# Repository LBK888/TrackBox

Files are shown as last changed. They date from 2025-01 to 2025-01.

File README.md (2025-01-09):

# TrackBox: An Open-Source Larvae Tracking and Monitoring System
For imaging zebrafish 6~7 dpf old zebrafish larvae

This project builds upon our preliminary research to further design and develop a versatile and cost-effective larvae tracking photography box compatible with 6-well and 24-well plates. 
The software includes a Python application for imaging and an Arduino IDE script for temperature and humidity recording. 
The initial versions of the software are openly available on here, while the hardware design is being updated to version 2.0:


## Key Features
- **Cost-Effective and Compatible**  
  Compatible with 6-well and 24-well plates, with material costs under 5000 TWD. For experiments using 6–7 days post-fertilization (dpf) zebrafish, each well can hold 5–7 fish, adjustable to 1–10 fish per well as needed.
- **Foldable and Portable Design**  
  The hardware features a foldable structure (Figure 14, bottom left), facilitating easy shipment to collaborating laboratories that cannot fabricate it themselves.  
- **Open Source**  
  Both hardware and software are open source and available on GitHub, with ongoing updates aligned with project milestones.  

## Technical Specifications
- **Camera**: SONY IMX179 sensor supporting 2592×1944 resolution at 20 fps. USB UVC-compatible, requiring no drivers for direct usage.  
- **Environment Monitoring**: Equipped with an AHT10 sensor to record temperature and humidity during imaging, ensuring experiments are conducted under stable environmental conditions.  
- **Lighting**: The base features an LED white light panel for uniform illumination.  
- **Multi-Box Support**: The imaging software supports simultaneous operation with 2–4 photography boxes, enhancing experimental efficiency.  

This system significantly reduces experimental costs and improves efficiency for zebrafish locomotion behavior studies. Contributions, feedback, and collaborations are welcomed!

## DIY Parts
- **3D printing**: See 3D parts folder
- **Laser cutting**: See Laser parts folder

## Electrical Parts
- **Camera**: USB 800 Megapixels ([DFROBOT FIT0729](https://www.dfrobot.com/product-2188.html))
- **Light box**: 15cm *2 - 5V COB 6000k (white light) LED stripe (5mm wide, 400 LED/meter), or 5050 LEDs 
- **Sensor**: (optional) temperature and humidity sensor, [AHT10](https://a.co/d/ckcVx5F)
- **MCU**: (optional) for temp+humid [D1 mini](https://a.co/d/eWSJpXV)

## Installation
Please read this [pdf manual](UpperPartInstructions.pdf) to assemble the upper part

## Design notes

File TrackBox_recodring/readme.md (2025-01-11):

# IMX179 Recording Program

## Overview
This program is designed for recording videos using the IMX179 camera (DFRobot FIT0729) along with temperature and humidity data collection. It supports the TrackBox v2.0 framework and is optimized for high-resolution video recording and real-time environmental data monitoring.

---

## Features
- **Camera Specifications**:
  - Max Resolution: 3264x2448 (8 Megapixels)
  - Video Output Format: AVI
  - Supported Resolutions & Frame Rates:
    - 3264x2448 @ 15fps
    - 2592x1944 @ 15fps
    - 1920x1080 @ 30fps
    - Additional resolutions supported.

- **Environment Data Logging**:
  - Reads temperature and humidity data via a serial connection.
  - Supports export to `.xlsx` files and visualizes data with plots.

- **Customizable Settings**:
  - Adjustable resolution, exposure, and recording duration.
  - Automatic and manual exposure control.
  - Configurable file output directories.

---

## Tested condition
- **Operating System**: Windows 11
- **Python Version**: 3.12.6
- **Hardware**: 
  - IMX179 Camera (DFRobot FIT0729)
  - MCU + AHT10 device for environment data collection (e.g., CH340 module)

### Python Dependencies
Install the required packages from the provided `requirements.txt` file:
pip install -r requirements.txt

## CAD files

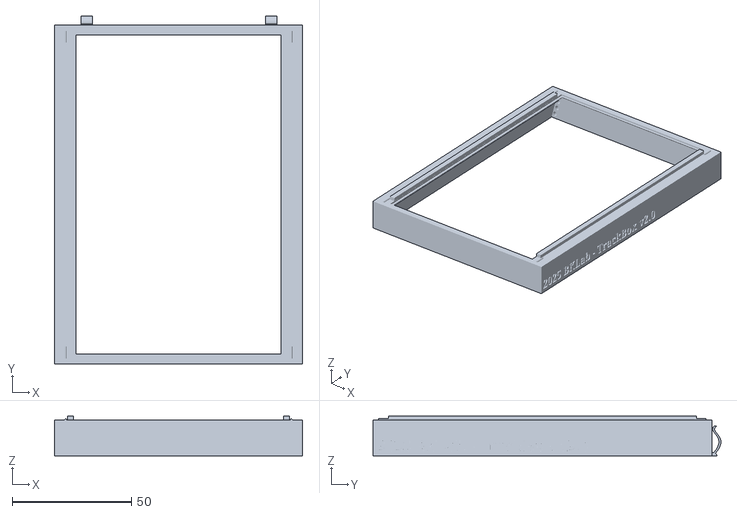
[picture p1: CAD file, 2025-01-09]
3D parts/LightBox v2.0_LightBox.stl
104.0 x 145.8 x 16.7

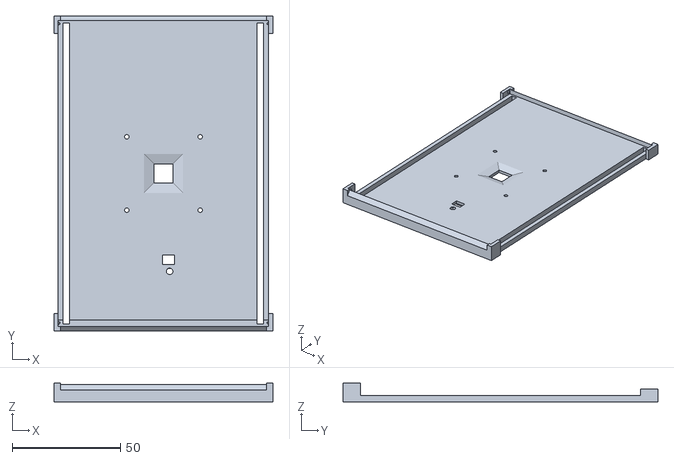
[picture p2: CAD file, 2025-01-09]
3D parts/LightBox v2.0_top2.stl
101.3 x 145.5 x 8.60

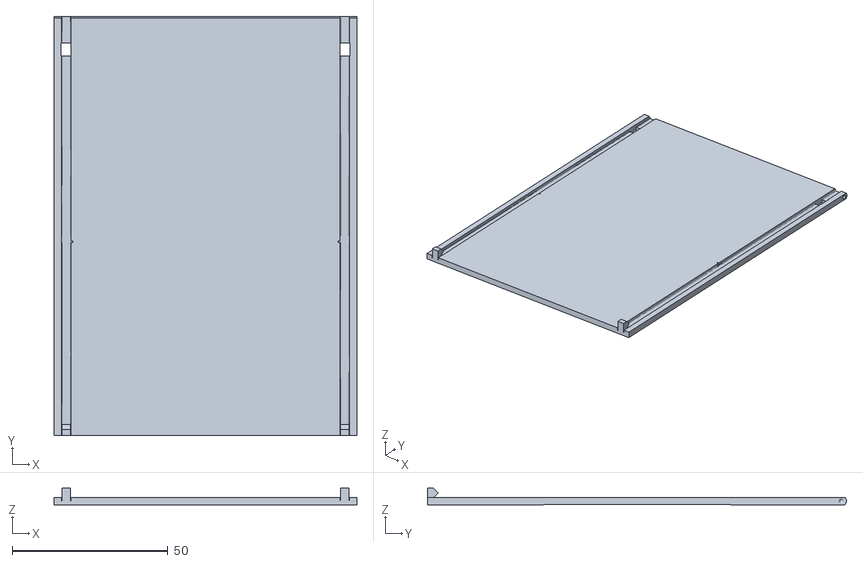
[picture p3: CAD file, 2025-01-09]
3D parts/LightBox v2.0_tall side.stl
97.2 x 134.5 x 5.30

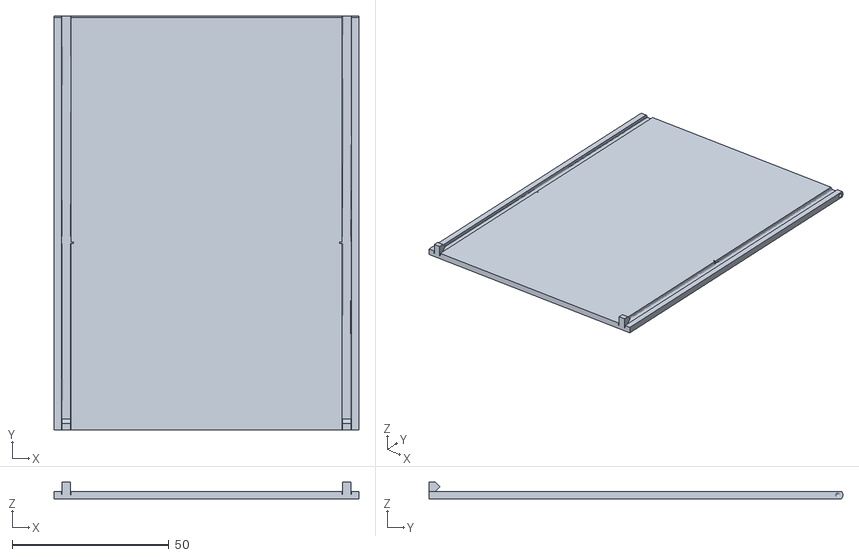
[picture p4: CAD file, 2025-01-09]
3D parts/LightBox v2.0_short side.stl
97.2 x 132.0 x 5.30

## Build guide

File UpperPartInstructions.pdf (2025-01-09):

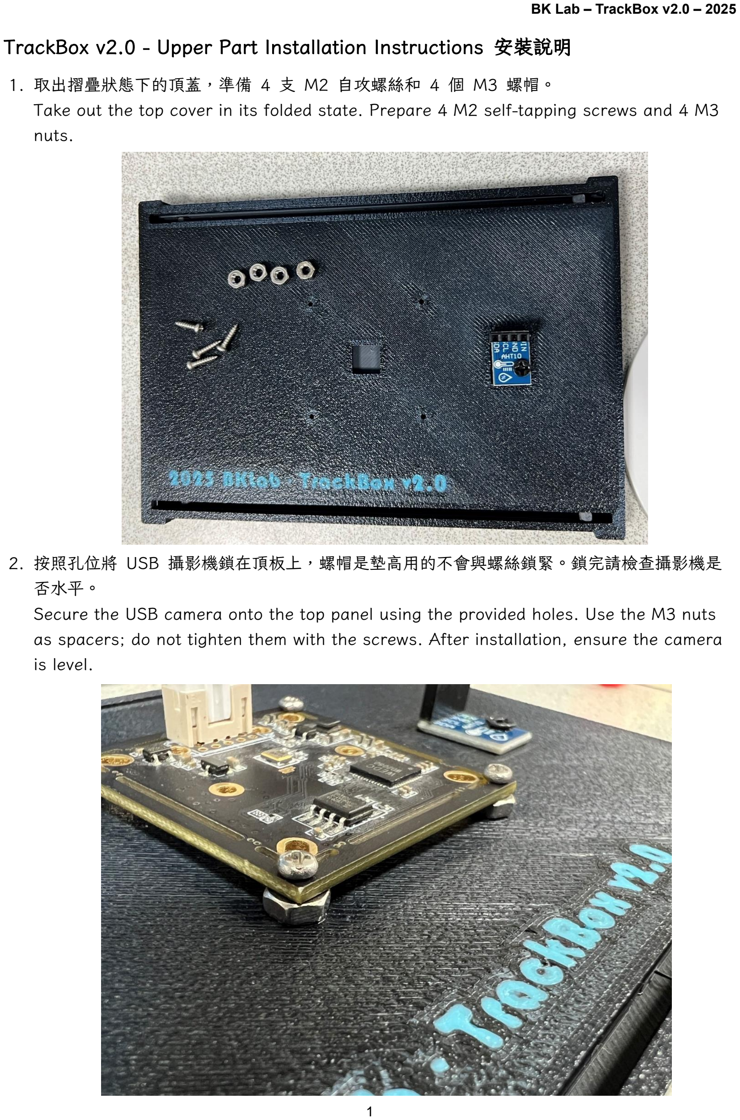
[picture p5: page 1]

BK Lab – TrackBox v2.0 – 2025
TrackBox v2.0 - Upper Part Installation Instructions 安裝說明
1. 取出摺疊狀態下的頂蓋，準備 4 支 M2 自攻螺絲和 4 個 M3 螺帽。
Take out the top cover in its folded state. Prepare 4 M2 self-tapping screws and 4 M3 nuts.
2. 按照孔位將 USB 攝影機鎖在頂板上，螺帽是墊高用的不會與螺絲鎖緊。鎖完請檢查攝影機是 否水平。
Secure the USB camera onto the top panel using the provided holes. Use the M3 nuts as spacers; do not tighten them with the screws. After installation, ensure the camera is level.

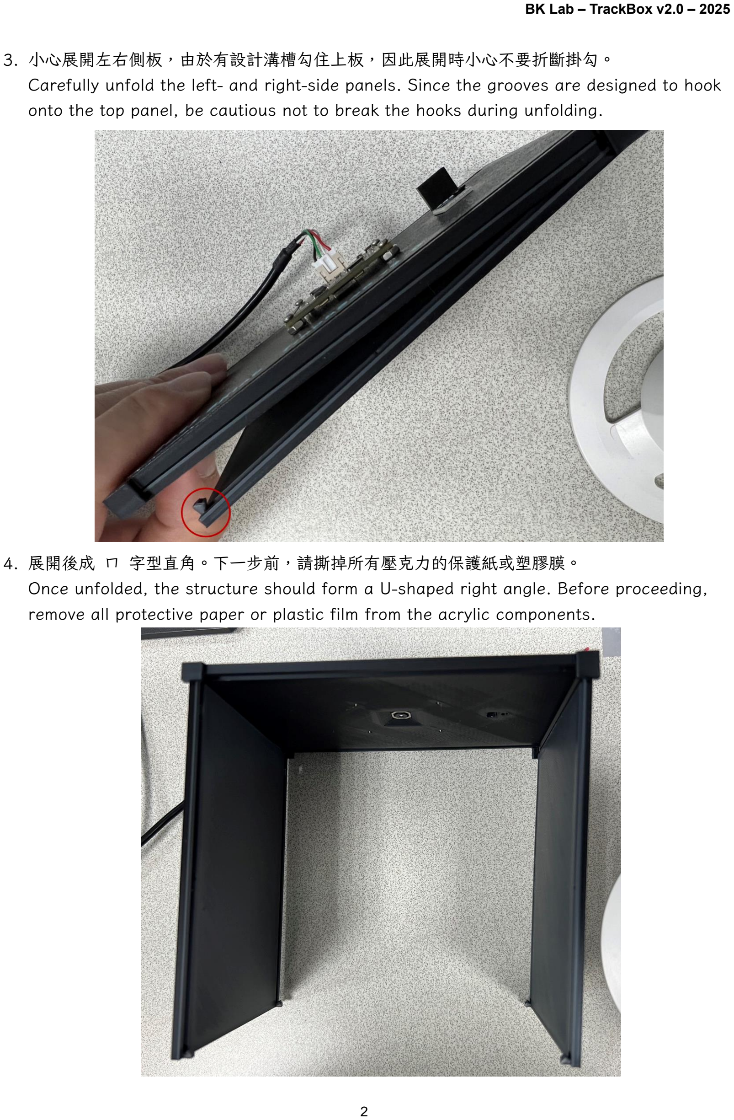
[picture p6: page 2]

3. 小心展開左右側板，由於有設計溝槽勾住上板，因此展開時小心不要折斷掛勾。 Carefully unfold the left- and right-side panels. Since the grooves are designed to hook onto the top panel, be cautious not to break the hooks during unfolding.
4. 展開後成 ㄇ 字型直角。下一步前，請撕掉所有壓克力的保護紙或塑膠膜。
Once unfolded, the structure should form a U-shaped right angle. Before proceeding, remove all protective paper or plastic film from the acrylic components.

5. 插入前後壓克力板，可選兩片皆不透光全黑色，或前側使用半透光。壓克力非亮面要朝向攝影 和內部以減少反光。
注意：這個步驟由於密合度高所以最為困難，請嘗試讓壓克力板剛進入時保持兩側深度一致。 如果左右側板被壓克力板推至脫落，請再左右側板卡回去即可。

Insert the front and rear acrylic panels. You can choose either fully opaque black panels for both or a semi-transparent panel for the front. Ensure the non-glossy side of the acrylic faces inward and toward the camera to reduce reflections.
Note: This step may be challenging due to the tight fit. If the side panels come loose, simply reattach them.
6. 前後壓克力板插入完成後，請注意前後面的四個接觸角落是否密合，確保攝影盒沒有形變。 After inserting the front and rear acrylic panels, check the four corner connections to ensure a tight fit. This ensures the photography box maintains its intended shape.

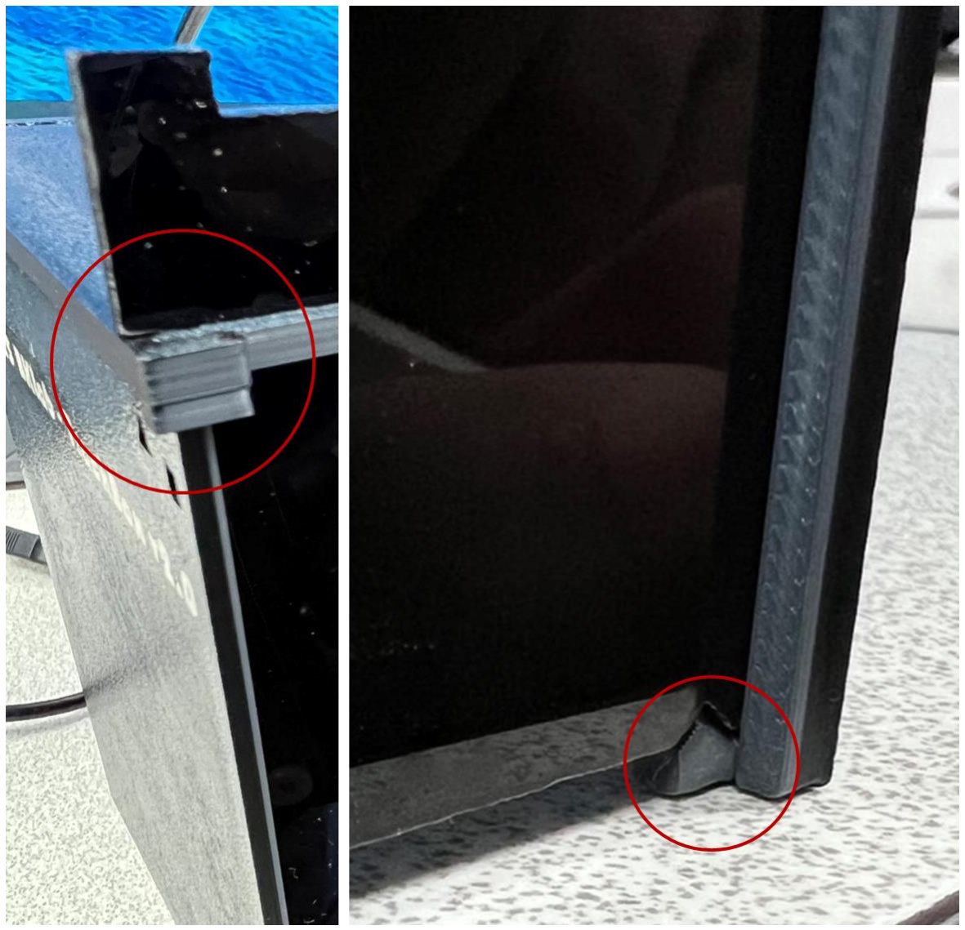
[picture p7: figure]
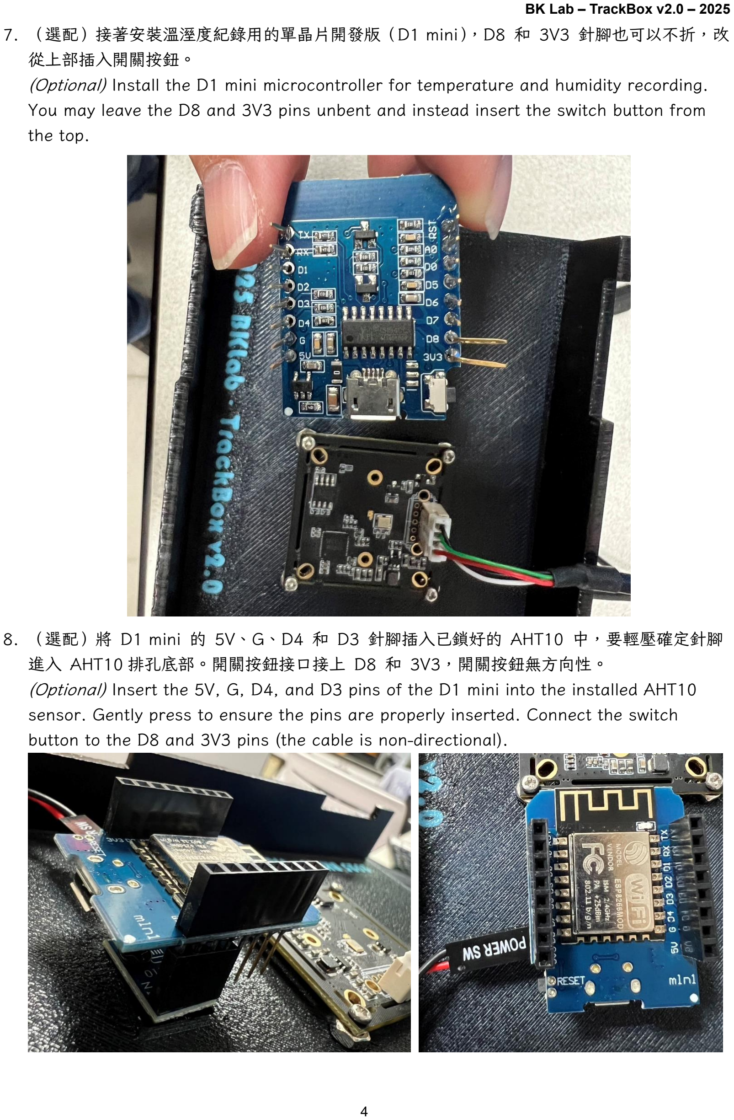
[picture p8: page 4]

7. （選配）接著安裝溫溼度紀錄用的單晶片開發版（D1 mini），D8 和 3V3 針腳也可以不折，改 從上部插入開關按鈕。
(Optional) Install the D1 mini microcontroller for temperature and humidity recording. You may leave the D8 and 3V3 pins unbent and instead insert the switch button from the top.
8. （選配）將 D1 mini 的 5V、G、D4 和 D3 針腳插入已鎖好的 AHT10 中，要輕壓確定針腳 進入 AHT10 排孔底部。開關按鈕接口接上 D8 和 3V3，開關按鈕無方向性。 (Optional) Insert the 5V, G, D4, and D3 pins of the D1 mini into the installed AHT10 sensor. Gently press to ensure the pins are properly inserted. Connect the switch button to the D8 and 3V3 pins (the cable is non-directional).

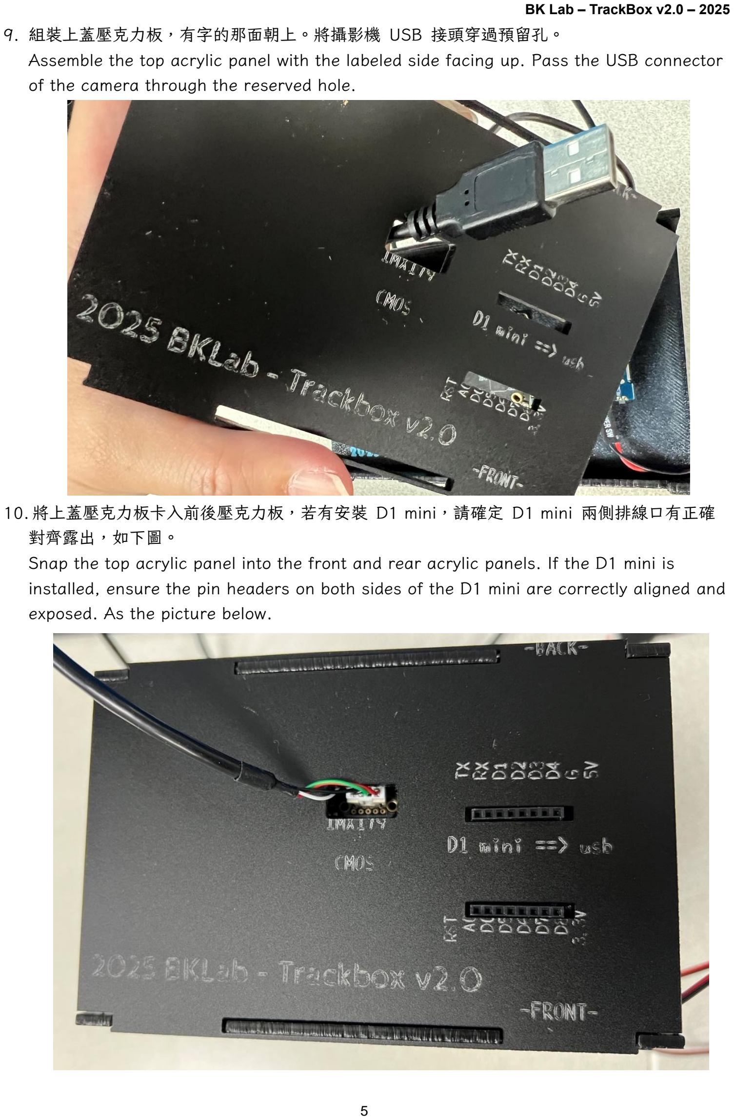
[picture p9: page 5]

9. 組裝上蓋壓克力板，有字的那面朝上。將攝影機 USB 接頭穿過預留孔。
Assemble the top acrylic panel with the labeled side facing up. Pass the USB connector of the camera through the reserved hole.
10. 將上蓋壓克力板卡入前後壓克力板，若有安裝 D1 mini，請確定 D1 mini 兩側排線口有正確 對齊露出，如下圖。
Snap the top acrylic panel into the front and rear acrylic panels. If the D1 mini is installed, ensure the pin headers on both sides of the D1 mini are correctly aligned and exposed. As the picture below.

11. （選配）將 D1 mini 接上 micro USB 線，連上電腦，序列埠通訊 115200 baud 可看到溫 溼度感測器資訊，如下圖。
(Optional) Connect the D1 mini to a computer using a micro USB cable. Use serial communication at 115200 baud to view the temperature and humidity sensor readings. As the picture below.

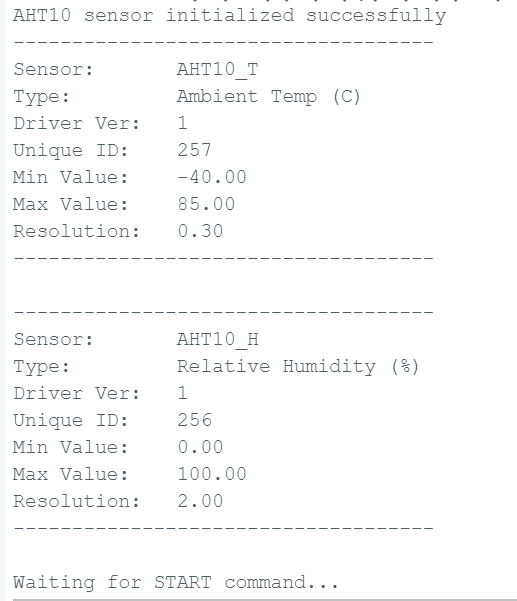
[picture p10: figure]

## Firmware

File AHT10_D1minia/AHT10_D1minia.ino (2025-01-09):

#include <Wire.h>
#include <Adafruit_AHT10.h> // 使用 AHT10 的庫，需要先安裝 (可從 Library Manager 搜尋 "AHT10")

#define SDA_PIN D3         // I²C SDA 腳位
#define SCL_PIN D4         // I²C SCL 腳位
#define BUTTON_PIN D8      // 按鈕開關接 D8 (GPIO15)
#define LED_PIN D2      // 測量指示燈, LED_BUILTIN=D4已經被佔據 


Adafruit_AHT10 aht10;               // 初始化 AHT10 物件
Adafruit_Sensor *aht_humidity, *aht_temp;

bool isMeasuring = false;  // 測量狀態標誌
float filter_r=0.3;     //smoothing filter, 前一次數據，站新數據的filter_r, recommand = 0.2~0.5
float temperature_rec=0.0;
float humidity_rec=0.0;

void setup() {
  // 初始化序列埠
  Serial.begin(115200);
  while (!Serial); // 等待序列埠初始化（適用於部分開發板）

  //Measuring LED
  pinMode(LED_PIN, OUTPUT);  // Initialize the LED_PIN pin as an output

  // 初始化按鈕腳位
  pinMode(BUTTON_PIN, INPUT); // 按鈕接 3.3V，利用內建下拉電阻

  // 初始化 I²C
  Wire.begin(SDA_PIN, SCL_PIN);
  Serial.println("I2C Initialized");

  // 初始化 AHT10
  if (aht10.begin()) {
    Serial.println("AHT10 sensor initialized successfully");
  } else {
    Serial.println("Failed to initialize AHT10 sensor!"); 
    while (1) { 
      delay(50);   // 如果感測器初始化失敗，停止執行
    }
  }

  aht_temp = aht10.getTemperatureSensor();
  aht_temp->printSensorDetails();

  aht_humidity = aht10.getHumiditySensor();
  aht_humidity->printSensorDetails();

  Serial.println("Waiting for START command...");


    //  /* Get a new normalized sensor event */
    sensors_event_t humidity;
    sensors_event_t temp;
    aht_humidity->getEvent(&humidity);
    aht_temp->getEvent(&temp);

    temperature_rec = temp.temperature; // 讀取溫度
    humidity_rec = humidity.relative_humidity;       // 讀取濕度
}

void loop() {
  // 檢查按鈕狀態
  if (digitalRead(BUTTON_PIN) == HIGH) { // 按鈕被按下（3.3V 高電平）
    delay(50); // 消除按鈕彈跳影響
    if (digitalRead(BUTTON_PIN) == HIGH) { // 確保按鈕保持按下狀態
      isMeasuring = !isMeasuring; // 切換測量狀態
      Serial.println(isMeasuring ? "Measuring started!" : "Measuring stopped!");
      delay(100); // 防止按鈕重複觸發
    }
  }

  // 檢查是否有來自 PC 的序列輸入
  if (Serial.available() > 0) {
    String command = Serial.readStringUntil('\n'); // 讀取指令
    command.trim(); // 去除多餘空白

    if (command == "START") {
      isMeasuring = true;
      Serial.println("Measuring started...");
    } else if (command == "STOP") {
      isMeasuring = false;
      Serial.println("Measuring stopped...");
    }
  }

  digitalWrite(LED_PIN, LOW); //先關燈

  // 如果處於測量狀態，讀取數據並發送
  if (isMeasuring) {
    digitalWrite(LED_PIN, HIGH);

    //  /* Get a new normalized sensor event */
    sensors_event_t humidity;
    sensors_event_t temp;
    aht_humidity->getEvent(&humidity);
    aht_temp->getEvent(&temp);

    //apply ratio filter to smooth the reading
    temperature_rec = temperature_rec*filter_r + temp.temperature*(1-filter_r); // 讀取溫度
    humidity_rec = humidity_rec*filter_r +humidity.relative_humidity*(1-filter_r);       // 讀取濕度

    // 傳送溫濕度數據到序列埠
    if (!isnan(temperature_rec) && !isnan(humidity_rec)) {
      Serial.print("Temperature: ");
      Serial.print(temperature_rec, 1); // 保留一位小數
      Serial.print(" °C, Humidity: ");
      Serial.print(humidity_rec, 1); // 保留一位小數
      Serial.println(" %");
    } else {
      Serial.println("Failed to read data from AHT10 sensor!");
    }

    delay(200); // 每0.2秒傳送一次數據
    digitalWrite(LED_PIN, LOW);
  }
}

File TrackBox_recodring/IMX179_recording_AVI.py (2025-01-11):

'''
IMX179 recording program - 2025.01.11 - version 1.0
 for TrackBox v2.0, https://github.com/LBK888/TrackBox
camera: IMX179 DFRobot FIT0729 (8 Megapixels USB Camera)

Max Effective Resolution: 3264(H) X 2448(V)  8 Megapixel
Image Output Format: JPEG 
Supported Resolution and Frame Rate: 
                 3264X2448 @ 15fps  / 2592X1944@ 15fps
                 1920x1080 @ 30fps  / 1600X1200@ 30fps
                 1280X720 @ 30fps  / 960X540@ 30fps
                 800X600 @ 30fps   / 640X480@ 30fps

To-Do:
    1. button control from MCU
    2. config file
'''
import cv2
import time
import os
import serial   #this is pyserial, not serial
from serial.tools import list_ports
from datetime import datetime
from openpyxl import Workbook
from openpyxl.chart import LineChart, Reference
import matplotlib.pyplot as plt
import csv
import threading
from queue import Queue
       

### USER Settings ###
# 設定時間間隔（10 分鐘）
RecDuration_min = 10
# 設定錄影解析度
width, height = 2592, 1944
# 設定曝光值 (可選)
auto_exposure=False  #是否自動曝光，若亮度不足導致曝光值>-4，可能會使fps不足
exposure_value = -7  # 曝光值通常在 -7 到 7 之間
# 相機號碼，預設=0，如像是筆電已有內建相機，請自行修改
camera_id=0
# 重要: 第一次錄影完，查看real FPS是多少，再來修改這裡
# 說明: 真實fps除了與硬體有關外，也與python+cv2版本有關，最佳組合可以達到2592*1944@19fps
fps=20.0
# 設定相機啟動後所需的自動對焦/曝光時間 (秒)
cam_pause=2.5

#folder
out_filename='video_' #prefix, 會檢查檔案不被複寫
#root path, 與本py檔同一資料夾，請放置於SSD硬碟
rootdir=os.path.dirname(os.path.realpath(__file__))+'/'
#folder
folder=rootdir
#folder='D:/Webcam_recodring/'  #請使用SSD硬碟

### Not Settings ###
RecDuration = RecDuration_min * 60

class VideoRecorder:
    def __init__(self):
        # 新增序列埠設定
        self.SERIAL_PORT = find_serial_port()
        self.BAUD_RATE = 115200
        self.ser = None
        self.temp_humid_data = []
        self.TH_read_intv=5 #溫溼度讀取間格，sec
        self.last_temp_read_time = 0  # 新增：追蹤上次讀取時間

        self.fn_code="1"

        # recording optimization
        self.frame_queue = Queue(maxsize=128)  # 新增 frame 佇列
        self.is_recording = True
        #self.buffer_size = 10  # 設定緩衝區大小        
        
        self.cleanup_handlers = []
        
    def setup_serial(self):
        """設置序列埠連接"""
        try:
            self.ser = serial.Serial(self.SERIAL_PORT, self.BAUD_RATE, timeout=1)
            time.sleep(2)  # 等待設備初始化
            self.ser.write(b"START\n")
            print("序列埠連接成功")
            return True
        except Exception as e:
            print(f"序列埠連接失敗: {e}")
            return False

    def read_temp_humid(self):
        """讀取溫溼度數據，每TH_read_intv秒執行一次"""
        current_time_TH = time.time()
        # 如果距離上次讀取還不到TH_read_intv秒，則跳過
        if current_time_TH - self.last_temp_read_time < self.TH_read_intv:
            return None, None
                
        if self.ser:
            try:
                # 清空緩衝區
                self.ser.reset_input_buffer()
                
                # 嘗試不同的編碼方式
                try:
                    line = self.ser.readline().decode('utf-8', errors='ignore').strip()
                except UnicodeDecodeError:
                    try:
                        line = self.ser.readline().decode('big5', errors='ignore').strip()
                    except UnicodeDecodeError:
                        line = self.ser.readline().decode('ascii', errors='ignore').strip()
                
                # 確保數據格式正確
                #print(line)
                if ":" in line and "," in line:
                    parts = line.split(", ")
                    if len(parts) >= 2:
                        # 使用更安全的方式提取數值
                        temp_str = parts[0].split(": ")[-1].split(" ")[0]
                        humid_str = parts[1].split(": ")[-1].split(" ")[0]
                        
                        # 確保能轉換為浮點數
                        if temp_str and humid_str:
                            temperature = float(temp_str)
                            humidity = float(humid_str)
                            
                            current_time_str = datetime.now().strftime("%H:%M:%S")
                            self.temp_humid_data.append([current_time_str, temperature, humidity])
                            self.last_temp_read_time = current_time_TH
                            return temperature, humidity
                            
            except Exception as e:
                print(f"讀取溫溼度數據錯誤: {e}")
                print(f"原始數據: {self.ser.readline()}")  # 用於調試
        return None, None


    def capture_frames(self, cap):
        """專門負責擷取影像的執行緒"""
        while self.is_recording:
            ret, frame = cap.read()
            if not ret:
                break
            if not self.frame_queue.full():
                self.frame_queue.put(frame)


    
    def record(self):
        try:
            # 選擇 webcam
            cap = cv2.VideoCapture(camera_id)
            #cap.set(cv2.CAP_PROP_FPS, 10)
            actual_width, actual_height = set_resolution(cap, width, height)

            if auto_exposure:
                set_exposure(cap, set_auto_exposure(cap))
            else:
                set_exposure(cap, exposure_value)
                time.sleep(cam_pause)   #等待自動對焦與自動曝光
            
            # 啟動擷取影像的執行緒
            capture_thread = threading.Thread(target=self.capture_frames, args=(cap,))
            capture_thread.start()
            

            # start rec time, 定時器開始        
            startT = time.time()
            frame_wrote = 0
            
            # 設置序列埠
            self.setup_serial()

            # Set Window size to 50％
            window_width = int(width * 0.5)
            window_height = int(height * 0.5)
            cv2.namedWindow('Webcam Recording', cv2.WINDOW_NORMAL)
            cv2.resizeWindow('Webcam Recording', window_width, window_height)

            self.fn_code=datetime.now().strftime('%Y%m%d_%H%M')
            filename = get_next_filename(folder+out_filename+self.fn_code+".avi")
            fourcc = cv2.VideoWriter_fourcc(*'XVID')
            out = cv2.VideoWriter(filename, fourcc, fps, (int(actual_width), int(actual_height)))

            while self.is_recording:
                #frame = None
                if not self.frame_queue.empty():    #opt..
                    frame = self.frame_queue.get()  #opt..
                    out.write(frame)
                    frame_wrote += 1
                    
                    if frame_wrote % 2 == 0:
                        cv2.imshow('Webcam Recording', frame)


                # 當前時間
                current_time = time.time() - startT

                # 如果是在攝影時間內則錄影
                if current_time >= RecDuration:
                    self.is_recording = False
                    break  # 達到指定錄製時間才結束


                #time.sleep(interval*0.1)

                # 按下 'q' 鍵結束錄影
                if cv2.waitKey(1) & 0xFF == ord('q'):
                    break

                # 讀取溫溼度
                temp, humid = self.read_temp_humid()
                if temp is not None and humid is not None:
                    print(f"溫度: {temp}°C, 濕度: {humid}%")

            # 釋放資源
            self.is_recording = False
            capture_thread.join()
            cap.release()
            out.release()
            cv2.destroyAllWindows()

            print(f'Vedio record and saved as {filename}')
            print(f'=> Total frame: {frame_wrote}')
            print(f'=> Total Duration: {current_time:.2f} sec')
            print(f'=> real FPS: {frame_wrote/current_time:.2f} fps')
        except Exception as e:
            print(f"錄影過程發生錯誤：{e}")
        finally:
            self.cleanup()

    def stop(self):
        # 儲存溫溼度數據
        if self.temp_humid_data:
            fn=f"temp_humid_{self.fn_code}"
            self.save_temp_humid_data(filename=fn+".xlsx")
            self.save_plot_data(filename=fn+".png")
        
        # 關閉序列埠
        if self.ser:
            self.ser.write(b"STOP\n")
            self.ser.close()


    def save_temp_humid_csv(self):
        """儲存溫溼度數據到 CSV 檔案"""
        filename = folder + f"temp_humid_{datetime.now().strftime('%Y%m%d_%H%M')}.csv"
        with open(filename, 'w', newline='') as f:
            writer = csv.writer(f)
            writer.writerow(['Time', 'Temperature (°C)', 'Humidity (%)'])
            writer.writerows(self.temp_humid_data)
        print(f"溫溼度數據已儲存至 {filename}")

    def save_temp_humid_data(self, filename="temp_humid.xlsx"):
        """將數據保存到 Excel 並繪製圖表"""
        wb = Workbook()
        ws = wb.active
        ws.title = "Temperature & Humidity"

        # 標題
        ws.append(["Time", "Temperature (°C)", "Humidity (%)"])

        # 插入數據
        for record in self.temp_humid_data:
            ws.append(record)

        # 繪製圖表
        chart = LineChart()
        chart.title = "Temperature & Humidity Over Time"
        chart.style = 12
        
        # 修改 y 軸設定
        chart.y_axis.title = "Value"
        #chart.y_axis.majorGridlines = True  # 修改：啟用網格線
        chart.y_axis.delete = False  # 修改：確保顯示 y 軸
        
        # 修改 x 軸設定
        chart.x_axis.title = "Time"
        chart.x_axis.tickLblPos = "low"
        chart.x_axis.tickLblSkip = 2
        #chart.x_axis.majorGridlines = True  # 修改：啟用網格線
        chart.x_axis.delete = False  # 修改：確保顯示 x 軸

        # 參考範圍（時間不包括在內）
        data_length = len(self.temp_humid_data)
        data_range = Reference(ws, min_col=2, max_col=3, min_row=1, max_row=data_length + 1)
        chart.add_data(data_range, titles_from_data=True)

        # 時間軸
        time_range = Reference(ws, min_col=1, min_row=2, max_row=data_length + 1)
        chart.set_categories(time_range)
        
        # 設定線條顏色
        s1 = chart.series[0]  # 溫度線
        s2 = chart.series[1]  # 濕度線
        s1.graphicalProperties.line.solidFill = "8B0000"  # 深紅色
        s2.graphicalProperties.line.solidFill = "87CEEB"  # 水藍色

        ws.add_chart(chart, "E5")
        wb.save(folder+filename)
        print(f"數據已保存為: {filename}")


    def save_plot_data(self, filename="temp_humid.png"):
        """用 matplotlib 繪製圖表"""
        if not self.temp_humid_data:  # 檢查是否有數據
            print("沒有可用的溫溼度數據")
            return
            
        times = [record[0] for record in self.temp_humid_data]
        temperatures = [record[1] for record in self.temp_humid_data]
        humidities = [record[2] for record in self.temp_humid_data]

        plt.figure(figsize=(12, 6))  # 修改：增加圖表大小
        plt.plot(times, temperatures, color='darkred', marker='o', label="Temperature (°C)", linewidth=2, markersize=6)
        plt.plot(times, humidities, color='skyblue', marker='o', label="Humidity (%)", linewidth=2, markersize=6)
        
        plt.xlabel("Time", fontsize=12)
        plt.ylabel("Value", fontsize=12)
        plt.title("Temperature & Humidity Over Time", fontsize=14)
        plt.legend(fontsize=10)
        plt.grid(True, linestyle='--', alpha=0.7)
        
        # 修改：調整x軸標籤
        plt.xticks(rotation=45, ha='right')
        
        # 修改：調整圖表邊距
        plt.tight_layout(pad=2.0)
        
        # 保存圖表
        plt.savefig(folder+filename, dpi=480, bbox_inches='tight')
        plt.close()  # 修改：關閉圖表，避免顯示
        print(f"圖表已保存為: {filename}")

    def cleanup(self):
        # 清理所有資源
        self.frame_queue.queue.clear()
        self.temp_humid_data = []
        self.is_recording = False
        
        self.ser.write(b"STOP\n")
        self.ser.close()
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
